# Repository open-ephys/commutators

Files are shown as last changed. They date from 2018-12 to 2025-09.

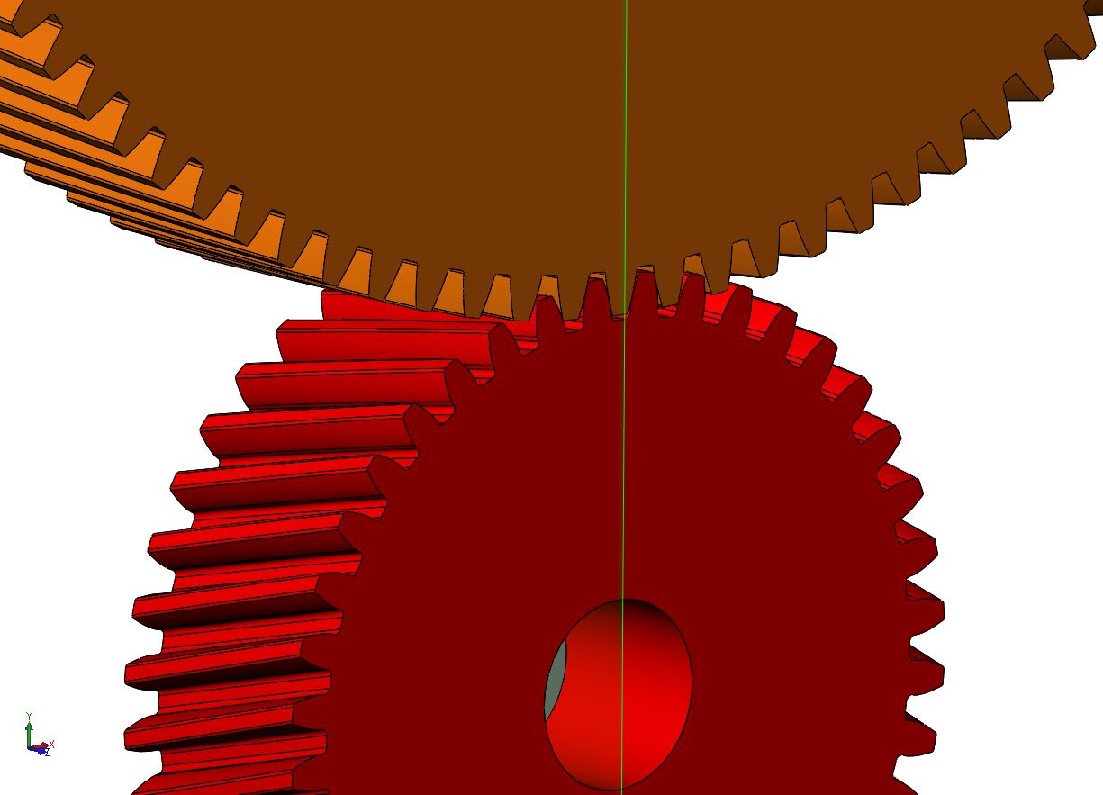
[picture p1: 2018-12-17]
mechanical/single_channel/gears/Robust Involute Helical Gear Generator.JPG

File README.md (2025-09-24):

> [!Important]  
> This repository has been split into dedicated repositories for each design:
>
>  - https://github.com/open-ephys/commutator-coax
>  - https://github.com/open-ephys/commutator-spi
>  - https://github.com/open-ephys/commutator-dual
>  - etc.
>
> Future commutator designs, issue tracking, etc. will take place in those repositories.
> This repository is deprecated.

# Torque-free commutators for orientation-aware headstages and miniscopes
The wide-spread availability of 6 degree of freedom pose tracking using
internal-measurement units (IMUs) allows continuous monitoring of an animal's
rotational state in an environment. This obviates the need for tether torque
measurements to drive an active commutator since the rotational state of the
animal is known in real-time, and the commutator can simply follow along. This
permits the use of extremely thin [coaxial
tethers](http://www.axon-cable.com/en/02_products/06_coaxial-cables/02/index.aspx)
that cannot function with a standard active commutator because they are too
flexible to translate rotational torque.

Zero-torque coaxial commutator.

This commutator functions with headstages and miniscopes that provide
provide appropriate rotational tracking information. Currently
supported devices are next-generation, serialized headstages and miniscopes
such as [ONIX headstages](https://open-ephys.github.io/onix-docs/index.html), 
and UCLA Miniscope 4.0, and Open Ephys 3D low-profile SPI headstages.
However, this device operations completely independently from the headstage
itself, so can be used with any device that provides accurate, drift-free
rotational state. It can even be used without an IMU, e.g. using video-based
rotation tracking since its remote control interface is agnostic to how
rotational measurements are taken.

## Features
- Variants for high bandwidth RF links up to 18 GHz and low-bandwidth SPI cables
- Optical table & 80/20 rail mountable
- Remote control using JSON-encoded commands
- Manual control using capacitive sense buttons
- Indication LED
    - Can be completely turned off
- Advanced stepper driver (TMC2130)
    - Voltage-controlled for silent operation
    - Precise motion using step interpolation (256 uSteps/step)
- USB powered and controlled
    - Internal super-capacitor circuitry prevents loading the USB bus during
      motion

## Usage

**Note**: A high-quality, within-spec micro USB cable must be used when connecting 
the commutator to the host computer.

### LED
The LED tells you about the commutator state:

1. Flashing red (*Charging*): commutator is charging internal super-capacitors.
   All controls and motor operation are locked. Wait until this process
   completes to use the device. It can take up to 30 seconds.
1. Solid red (*Disabled*): commutator is disabled. Motor is turned off and will not
   turn or respond to button presses or external commands.
1. Green (*Enabled*): commutator is enabled and permits both remote and manual
   (button) turn control. Buttons take precedence over remote commands.

### Buttons
The front panel has four buttons.

- __Enable/Disable__: toggle commutator enable/disable.
    - *Disabled* (LED is red): All motor output will halt instantly, and motor
      driver is powered down. Pressing directional buttons in the stopped state
      will not work. All target turns provided via remote calls will be
      cleared, such that re-enable the motor will not result in the commutator
      re-engaging an old target position. In this state, pressing 
      the Enable/Disable button, or sending the approriate remote
      command, will enable the device.
    - *Enabled* (LED  green): When in the *enabled* state, the LED will be
      green and the motor can be turned via button presses or RPCs . In this
      state, pressing the Stop/Go button, or sending the approriate remote
      command, will instantly disable the device.

- __Directional__ (2x): Manually control the motor rotation in the
  direction indicated on each button when the commutator is *Enabled*. These
  inputs take precedence over and override ongoing remote motor control.  When
  pressed, all target turns provided via remote control will be cleared, such
  that releasing them will not result in the commutator re-engaging an old
  target position. Remote commands sent when a button is being pressed are
  ignored.

- __LED__: pressing the LED will toggled on and off (e.g for cases where it presents an
  unwanted visual stimulus).

### Remote control interface
When manual buttons are not being pressed, the commutator accepts JSON-encoded
commands over its serial interface. Here are examples of all commands that can
be sent:
```
{enable : true}     // Enable commutator (default = false)
{led : false}       // Turn off RGB LED (default = true)
{speed : 250}       // Set turn speed to 250 RPM (default = 50 RPM, valid ∈ (0, 500] RPM)
{turn : 1.1}        // 1.1 turns CW
{turn : -1.1}       // 1.1 turns CCW

// Example multi-command. Any combo can be used.
// In this case:
// 1. Turn LED off
// 1. Set speed to 25 RPM
// 2. Excecute 1.1 turns CC
// Ordering of commands does not matter, it is determined by the firmware
{led: false, speed: 25, turn : -1.1}
```
The communator state can be read using the `{print:}` command  which will
return a JSON object containing version, state, and motor parameters.

### Saving settings
All control and speed parameters, whether changed via the remote or manual
interface, are saved in non-volatile memory each time they are changed. The
device will start in the same state it was last used.

## Firmware
The controller firmware is located [here](./firmware/commutator). It runs on a
[Teensy lc](https://www.pjrc.com/store/teensylc.html). To compile
this firmware and program the microcontroller, you need the following
dependencies:

- [Arduino IDE](https://www.arduino.cc/en/Main/Software)
- [Teensyduino add-on](https://www.pjrc.com/teensy/td_download.html)
- [AccelStepper](https://www.airspayce.com/mikem/arduino/AccelStepper/)
- [Arduino JSON](https://arduinojson.org/)

The firmware can be uploaded to the device using the [Arduino
IDE](https://www.arduino.cc/en/Main/Software). _Note that you will need to add
the [Teensyduino add-on](https://www.pjrc.com/teensy/teensyduino.html) to to
the Arduino IDE to program the Teensy_. When installing Teensyduino, you should
opt to install all of the bundled libraries as well. This takes care of
installing `AccelStepper` library rather than having to install it manually.
ArduinoJSON can be installed through the Arduino IDE's package manager.

## Construction

### Bill of Materials
The BOM is located [here](https://docs.google.com/spreadsheets/d/1M2R0Q2-OuRHzctt05BxtA3hxNcCHtRZHORzCKElmG1Q/edit#gid=1283420334).

### Mechanical
The mechanical component of the commutator are as follows:

1. RF Rotary Joint
1. 2x reduction gears (3D-printed)
1. NEMA-11 Stepper Motor
1. Housing (3D-printed)
1. Some fasteners

Mechanical designs are located [here](./mechanical/). STL files for 3D printing
are located in the `stl` subdirectory. Links to purchase each of these
components, including 3D-printed parts, can be found on the BOM.

### Electronics
The board used to control the commutator consists of the following elements:

1. [Teensy LC](https://www.pjrc.com/store/teensylc.html) for receiving
   commands and controlling all circuit elements.
1. [TMC2130 stepper driver](https://www.analog.com/media/en/technical-documentation/data-sheets/TMC2130_datasheet_rev1.15.pdf) for driving the
   motor.
1. Super-capacitor charge system and step-up regulator for providing
   high-current capacity drive to the motor driver directly from USB.
1. RGB indicator LED.
1. Capacitive touch sensors on the back side of the PCB that serve as buttons
   for manual commutator control

Board designs and manufacturing files are located [here](./pcb/). 

## Hardware License
This license pertains to documents in the `control-board`, `mechanical`, and
`resources` subdirectory.

This work is licensed to Jonathan P. Newman and Jakob Voigts under CC BY-NC-SA
4.0. To view a copy of this license, visit
https://creativecommons.org/licenses/by-nc-sa/4.0

The creation of commercial products using the hardware documentation in this
repository is not permitted without an explicit, supplementary agreement
between the Licensor and the Licensee. Please get in touch if you are
interested in commercially distributing this tool.

## Software/Firmware License
This license pertains to documents in the source code in the `firmware`
subdirectory.

Copyright Jonathan P. Newman

Permission is hereby granted, free of charge, to any person obtaining a copy of
this software and associated documentation files (the "Software"), to deal in
the Software without restriction, including without limitation the rights to
use, copy, modify, merge, publish, distribute, sublicense, and/or sell copies
of the Software, and to permit persons to whom the Software is furnished to do
so, subject to the following conditions:

The above copyright notice and this permission notice shall be included in all
copies or substantial portions of the Software.

THE SOFTWARE IS PROVIDED "AS IS", WITHOUT WARRANTY OF ANY KIND, EXPRESS OR
IMPLIED, INCLUDING BUT NOT LIMITED TO THE WARRANTIES OF MERCHANTABILITY,
FITNESS FOR A PARTICULAR PURPOSE AND NONINFRINGEMENT. IN NO EVENT SHALL THE
AUTHORS OR COPYRIGHT HOLDERS BE LIABLE FOR ANY CLAIM, DAMAGES OR OTHER
LIABILITY, WHETHER IN AN ACTION OF CONTRACT, TORT OR OTHERWISE, ARISING FROM,
OUT OF OR IN CONNECTION WITH THE SOFTWARE OR THE USE OR OTHER DEALINGS IN THE
SOFTWARE.

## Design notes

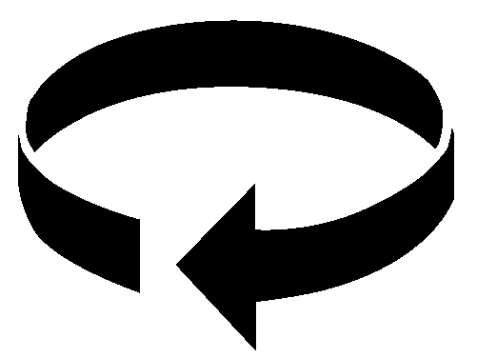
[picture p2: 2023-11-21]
pcb/images/turn-cw.png

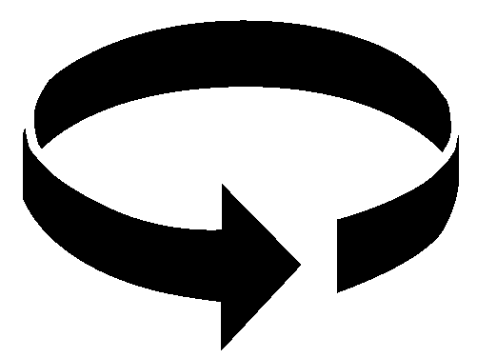
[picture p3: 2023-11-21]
pcb/images/turn-ccw.png

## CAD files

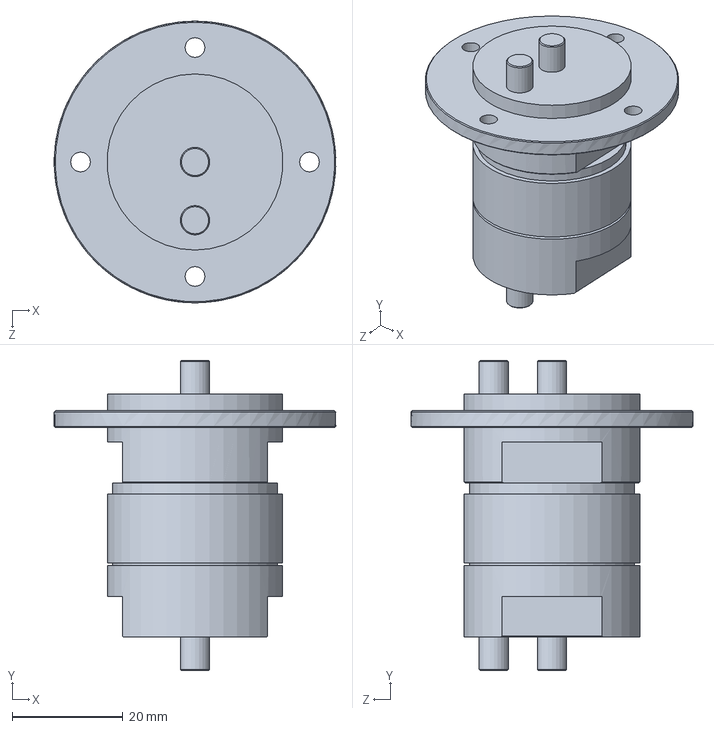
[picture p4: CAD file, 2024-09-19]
mechanical/dual_channel/BN_153127C0001_rotary_joint.SLDPRT
50.8 x 55.9 x 50.8 mm

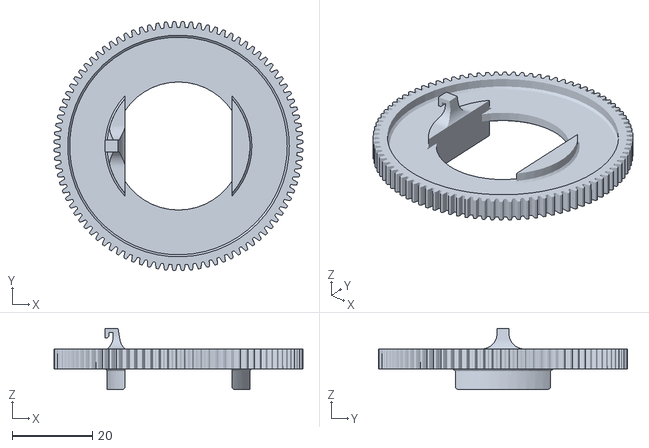
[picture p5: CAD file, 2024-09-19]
mechanical/dual_channel/STL/gear_b_dual_channel.STL
62.0 x 62.0 x 15.3

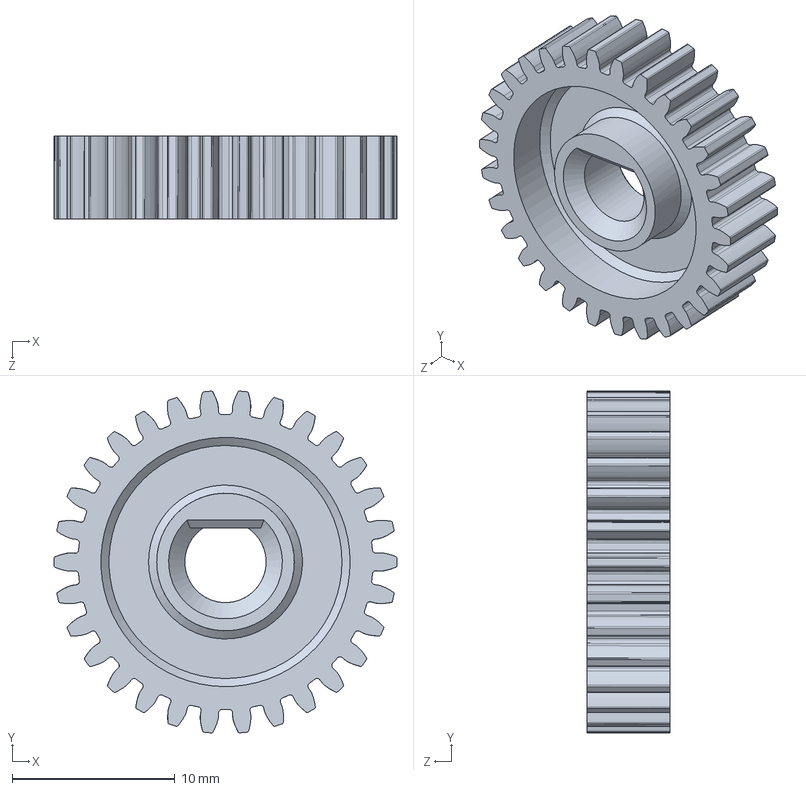
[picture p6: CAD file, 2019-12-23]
mechanical/single_channel/gears/gear_a.SLDPRT
21.1 x 21.0 x 5.08 mm

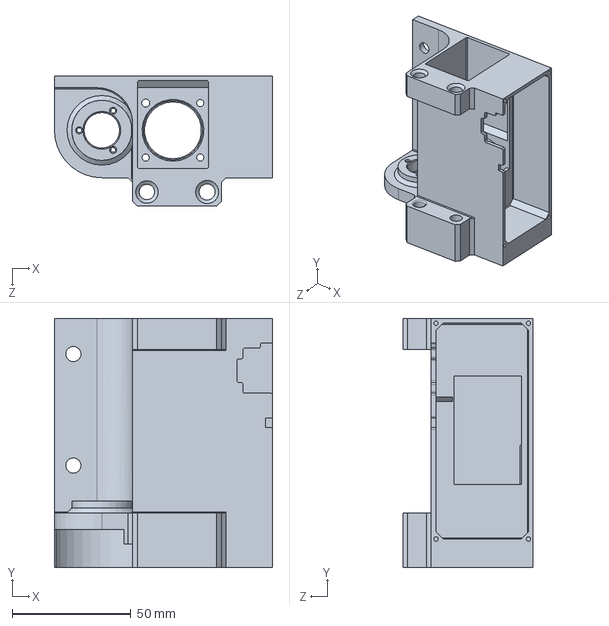
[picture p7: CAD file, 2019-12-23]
mechanical/single_channel/rf_commutator_housing.SLDPRT
92.0 x 105.0 x 55.0 mm

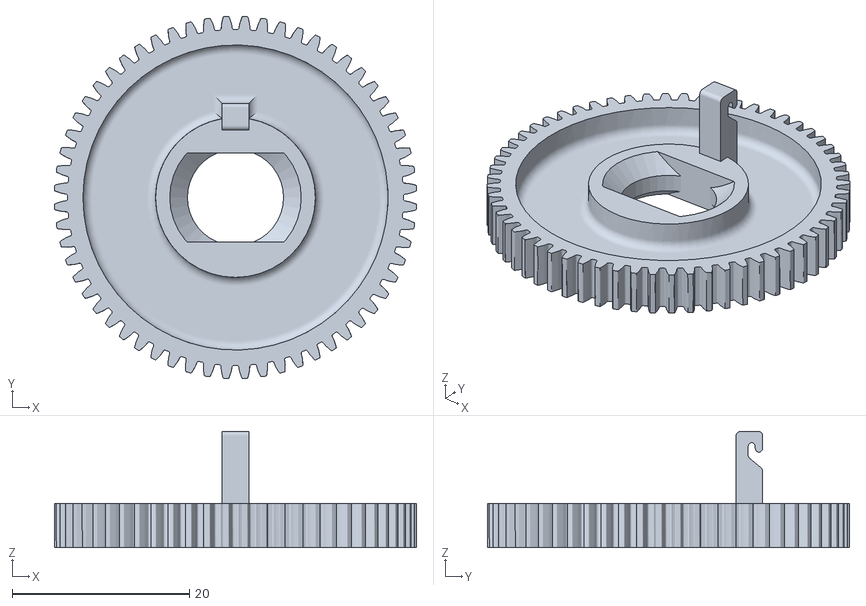
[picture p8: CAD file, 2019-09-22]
mechanical/single_channel/stl/gear_b.STL
40.9 x 40.9 x 13.1

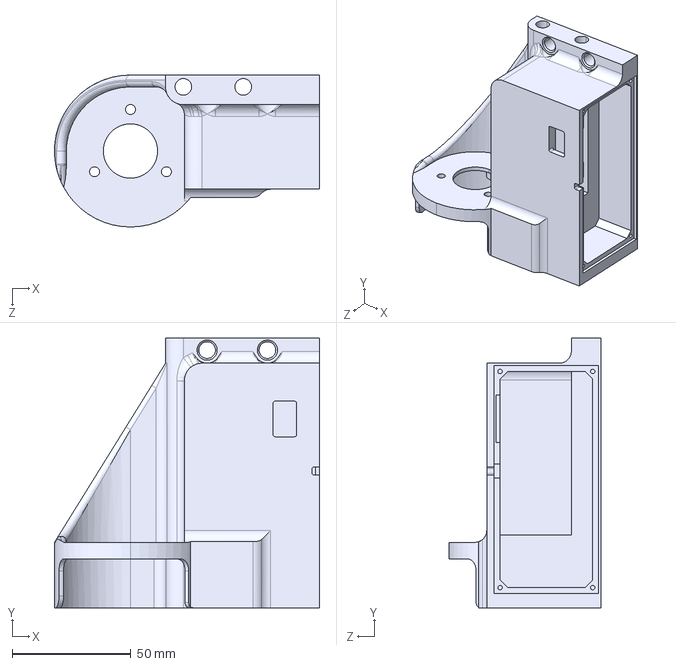
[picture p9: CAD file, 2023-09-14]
mechanical/spi/production/SPI Commutator Enclosure Motor Enclosed.STEP
111.6 x 113.5 x 64.0 mm

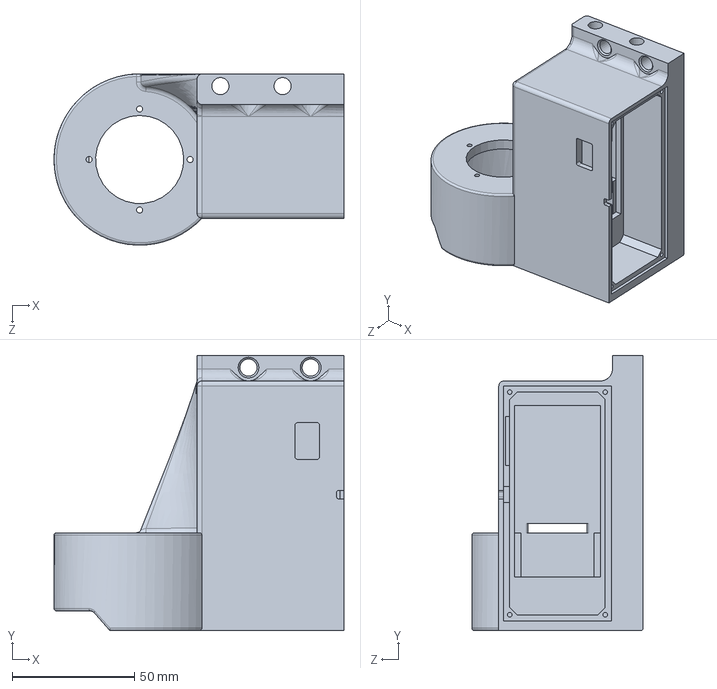
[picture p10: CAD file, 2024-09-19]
mechanical/dual_channel/dual_channel_commutator_housing.SLDPRT
118.5 x 112.5 x 70.0 mm

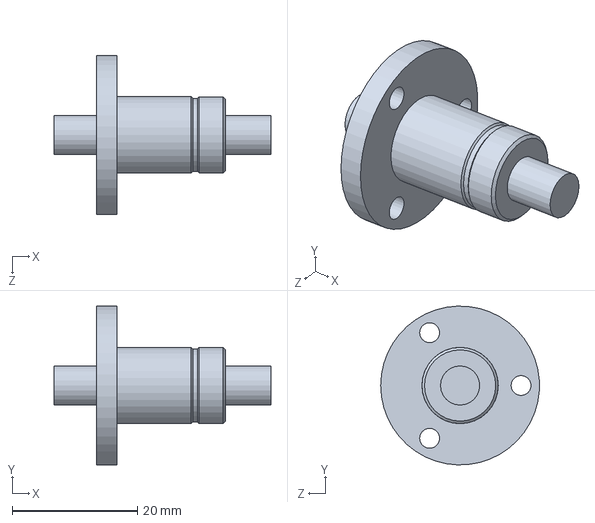
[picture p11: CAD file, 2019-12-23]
mechanical/single_channel/Fairview_FMRJ1002_rf_rotary_jpint_female_to_female_flanged.SLDPRT
34.7 x 25.4 x 25.4 mm

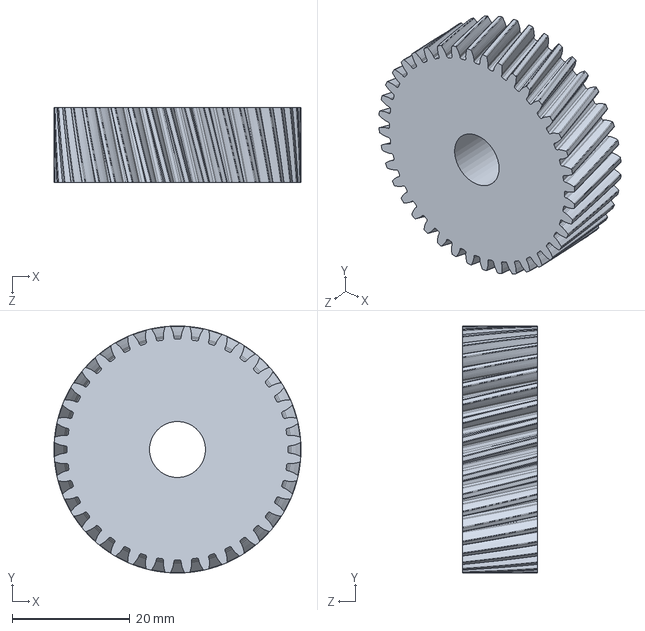
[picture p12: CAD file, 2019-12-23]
mechanical/single_channel/gears/Robust Involute Helical Gear Generator - CCW.SLDPRT
42.0 x 42.0 x 12.7 mm

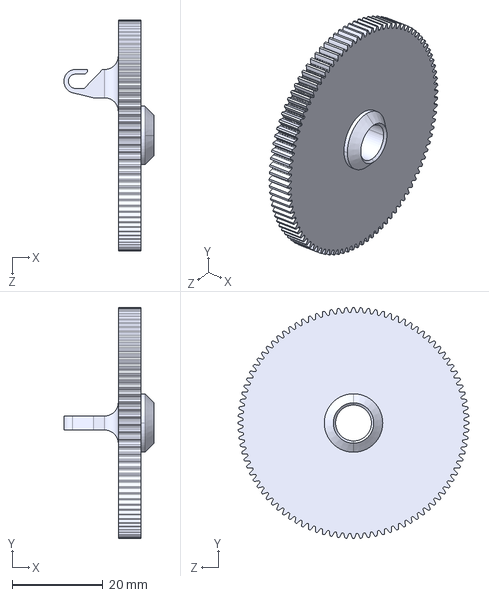
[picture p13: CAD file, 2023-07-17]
mechanical/spi/production/SI_sdpsi_s12a05m096n0310 cut.STEP
19.9 x 51.0 x 51.0 mm

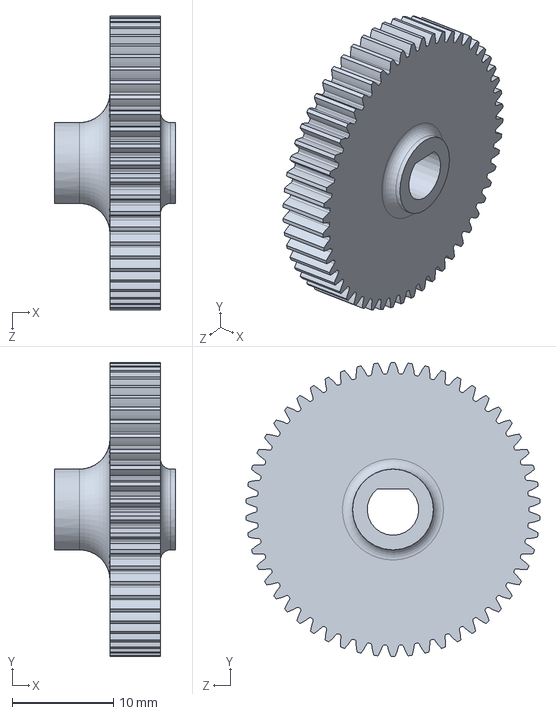
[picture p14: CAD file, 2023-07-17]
mechanical/spi/source/SI_sdpsi_s12a05m054n0310 cut.SLDPRT
12.0 x 29.1 x 29.1 mm

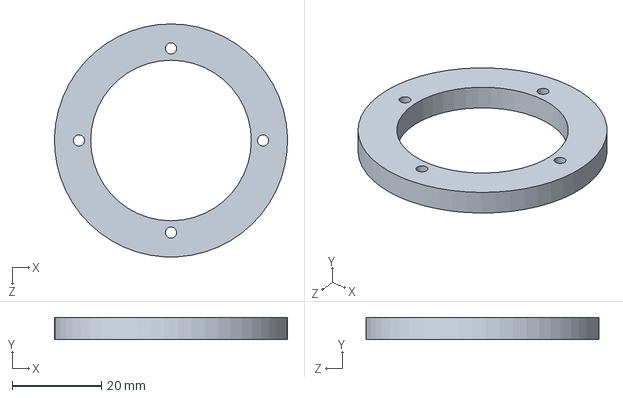
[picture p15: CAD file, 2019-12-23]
mechanical/dual_channel/dual_channel_commuttaor_housing.SLDPRT
52.2 x 5.00 x 52.3 mm

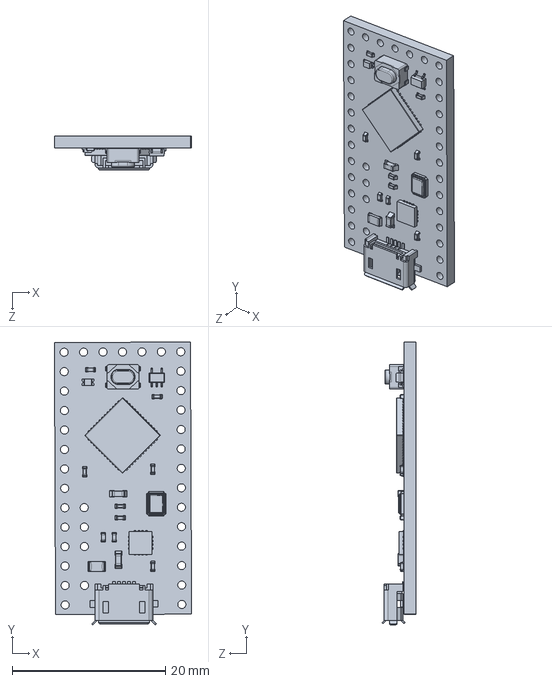
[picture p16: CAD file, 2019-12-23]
mechanical/single_channel/Teensy_lc.SLDPRT
17.9 x 37.0 x 4.49 mm

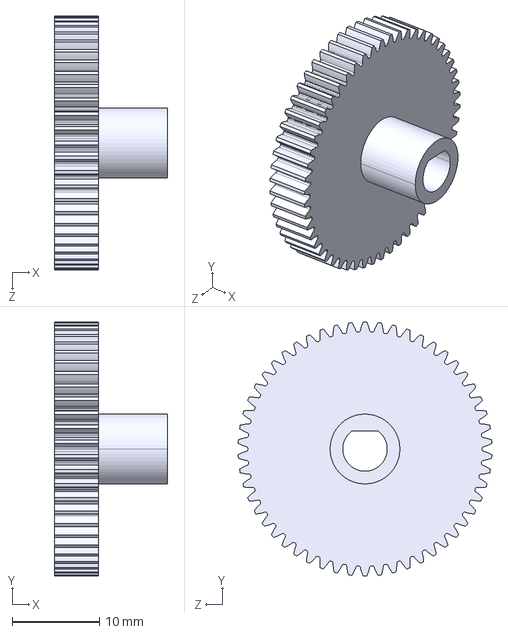
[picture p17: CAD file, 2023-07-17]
mechanical/spi/production/SI_sdpsi_s12a05m054n0310 cut.STEP
13.0 x 29.1 x 29.1 mm

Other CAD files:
mechanical/spi/source/SPI Commutator Enclosure Motor Enclosed.SLDPRT
mechanical/single_channel/stl/gear_a.STL
mechanical/single_channel/gears/gear_b.STL
mechanical/spi/source/SI_sdpsi_s12a05m096n0310 cut.STEP
mechanical/dual_channel/STL/dual_channel_commutator_housing.STL
mechanical/single_channel/6627T370_POSITION-CONTROL DC MOTOR.SLDPRT
mechanical/single_channel/CUI_PJ-102A.SLDPRT
mechanical/single_channel/CUI_PJ-102A.STEP
mechanical/single_channel/DRV 8825 With Headers Assem.SLDPRT
mechanical/single_channel/DRV 8825 With Headers Assem.STEP
mechanical/single_channel/Fairview_FMRJ1001_rf_rotary_jpint_female_to_female.SLDPRT
mechanical/single_channel/Teensy_lc.stp
mechanical/single_channel/pulley_large.SLDPRT
mechanical/single_channel/pulley_small.SLDPRT
mechanical/single_channel/spinner_BN-835047C0010_rf_rotary_joint.SLDPRT
mechanical/single_channel/stl/rf_commutator_housing.STL
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

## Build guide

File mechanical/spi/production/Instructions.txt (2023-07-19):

Printing Methods:
Gears - SLA
Enclosure - SLS

The gears are glued to the Orbex and motor shafts

Set gear ratio (16.0/9.0) using the GEAR_RATIO macro found on line 22 of https://github.com/open-ephys/onix-commutator/blob/master/firmware/commutator/commutator.ino (this is valid since commit f684f83; this could change if commutator firmware is updated)

All 11 holes need to be tapped. I'm not sure how OEPS does it for the Coax Commutator, but I assume whatever tool you use for that can be used for tapping the holes on the coax commutator
@Jon Newman I don't think I missed anything, but if you have anything add ^ feel free

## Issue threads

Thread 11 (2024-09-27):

### ISSUE TITLE
Teensy 3.2 and LC EOL 

### ISSUE THREAD

**Issue by jonnew** [open-ephys/commutators#11]
Both the Teensy LC and 3.2 are end of lifed. We will need to migrate to a different microcontroller option. Most MCUs don't come with integrated capacitive touch sensing. Additionally it has proven to be quite a difficult thing to get working reliably. However, it reducing design complexity and is appropriate for environments with animals. An option would be switching to some relatively generic MCU, e.g. RP2040 and adding an external cap sensor that hopefully takes care of the calibration issues for us. @aacuevas suggests the following: 

- https://ww1.microchip.com/downloads/aemDocuments/documents/OTH/ProductDocuments/DataSheets/00001571B.pdf

Microchip seems to have a family of those, which is a good thing for future-proofing. And it's a bit under a dollar and a half. In any case, it will need to be tested.

**Comment by jonnew** [comment]
Some measurements of GND referenced capacitance at on the V1.1 PCB

|   | 1 kHz   |
|---|---|
| LED Button  | 14 pF   | 
| Left Turn  |  51 pF | 
| Right Turn | 45 pF  | 
| Enable/Disable   | 42 pF  | 

This is right at the limit for the chip suggested above:

![image](https://github.com/user-attachments/assets/a6db75b4-fe4f-400c-8482-b05cc65772db)

Might be work decreasing this bit (e.g. by mesh filling the copy islands of the big buttons with ~50 fill density)

**Comment by cjsha** [comment]
Thanks for taking those measurements, I'll try the 50% mesh fill. That's also suggested by:
[Capacitive-Touch-Sensor-Design-Guide-DS00002934-B.pdf](https://github.com/user-attachments/files/17078185/Capacitive-Touch-Sensor-Design-Guide-DS00002934-B.pdf)
![Screenshot_20240920-123908](https://github.com/user-attachments/assets/18e2195d-66f2-4194-952a-0a322f52d42f)

**Comment by jonnew** [comment]
Nice, that guide is cool.

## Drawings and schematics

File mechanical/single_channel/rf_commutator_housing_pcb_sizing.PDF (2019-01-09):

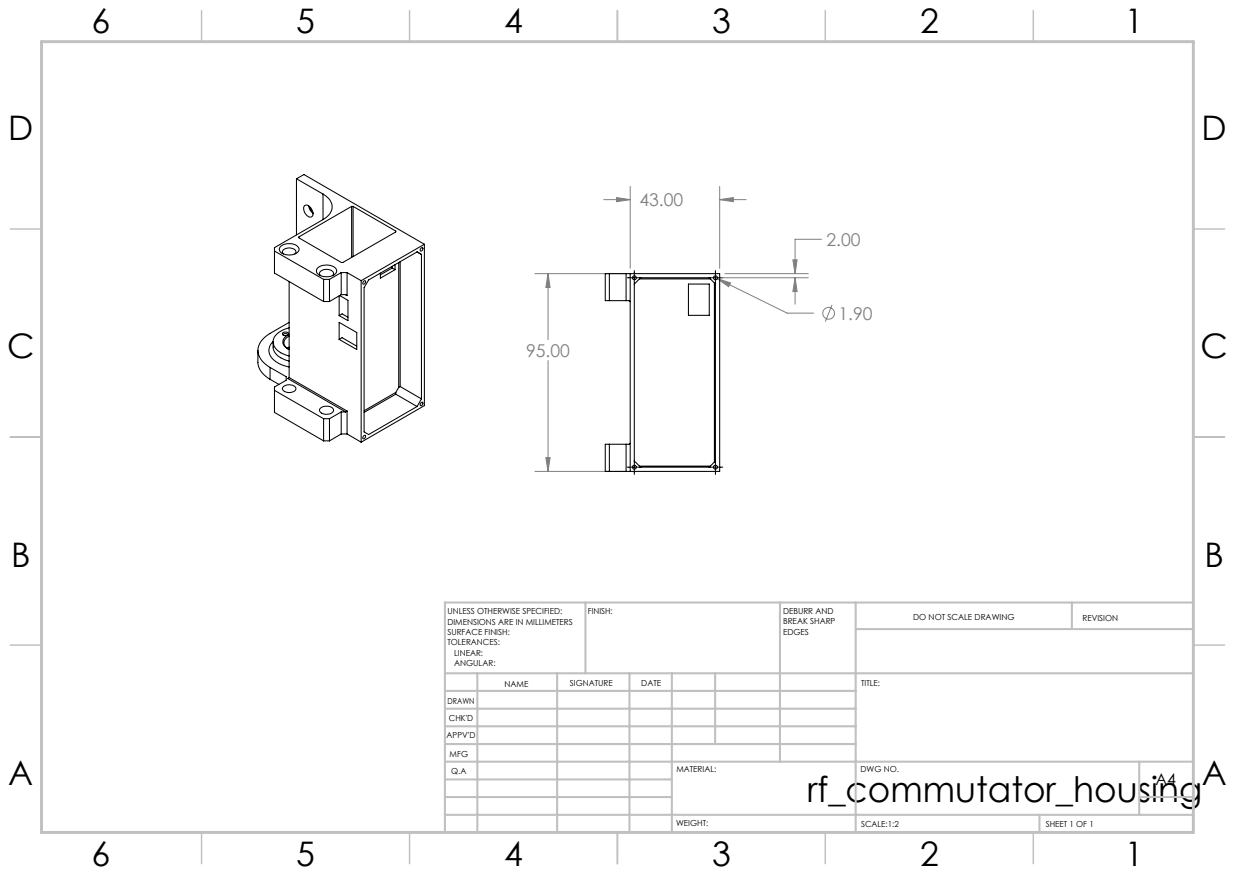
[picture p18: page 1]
FINISH:; DEBURR AND; BREAK SHARP; DO NOT SCALE DRAWING; REVISION; SCALE:1:2; SHEET 1 OF 1

UNLESS OTHERWISE SPECIFIED:
DIMENSIONS ARE IN MILLIMETERS
SURFACE FINISH:
TOLERANCES:
LINEAR:
ANGULAR:

NAME | SIGNATURE | DATE | | | | TITLE:

DRAWN
CHK'D
APPV'D
MFG
Q.A | | | | MATERIAL: | DWG NO. | A4

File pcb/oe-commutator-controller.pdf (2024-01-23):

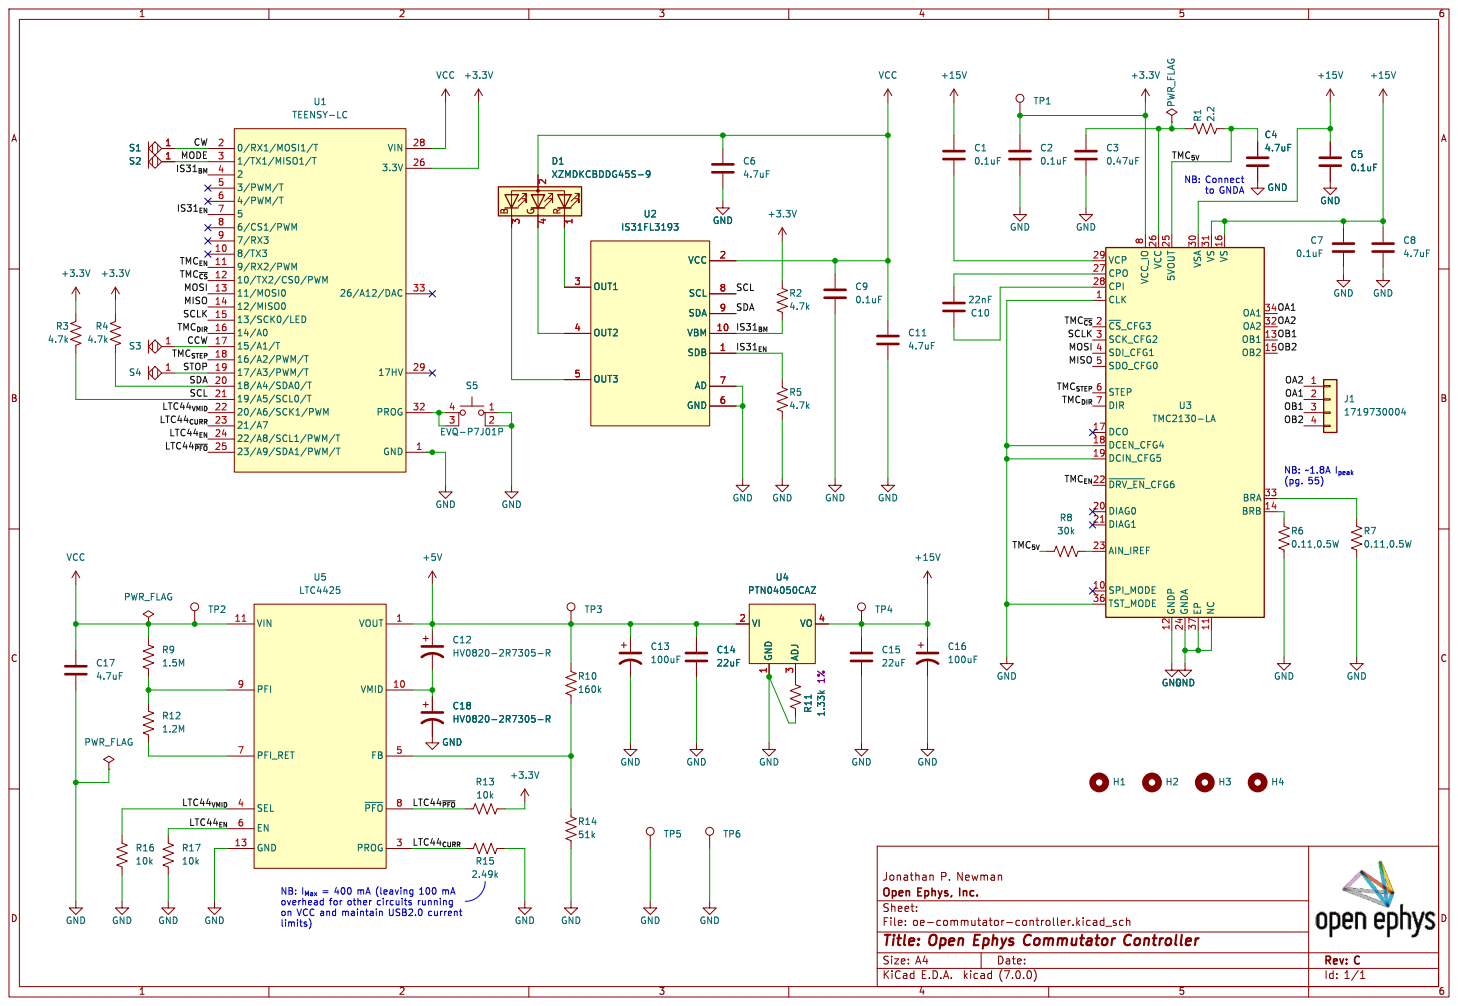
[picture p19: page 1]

(pg. 55) NB: I_{Max} = 400 mA (leaving 100 mA

overhead for other circuits running
on VCC and maintain USB2.0 current
limits)

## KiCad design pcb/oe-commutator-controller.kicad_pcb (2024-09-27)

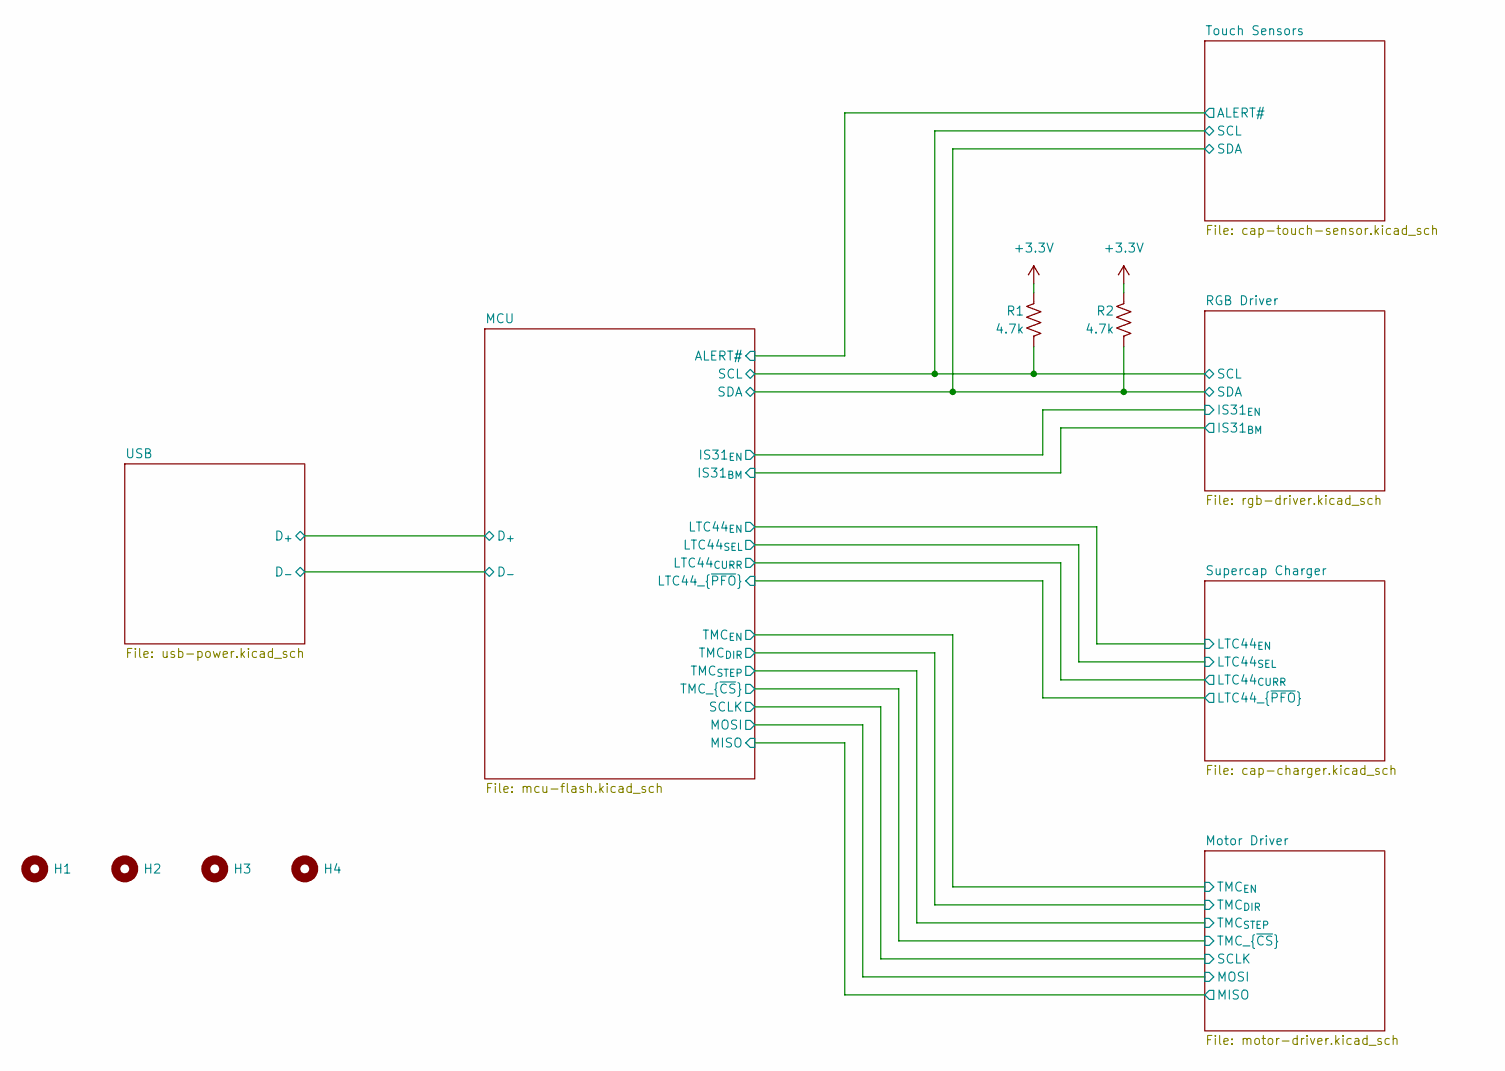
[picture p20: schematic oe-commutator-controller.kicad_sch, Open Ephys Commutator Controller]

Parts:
H1, H2, H3, H4: MountingHole_2.7mm_M2.5_ISO7380
R1, R2: 4.7k; R_0603_1608Metric

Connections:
+3.3V: R1.1, R2.1; also elsewhere on the board
/MCU/SCL: R1.2; also elsewhere on the board
/MCU/SDA: R2.2; also elsewhere on the board

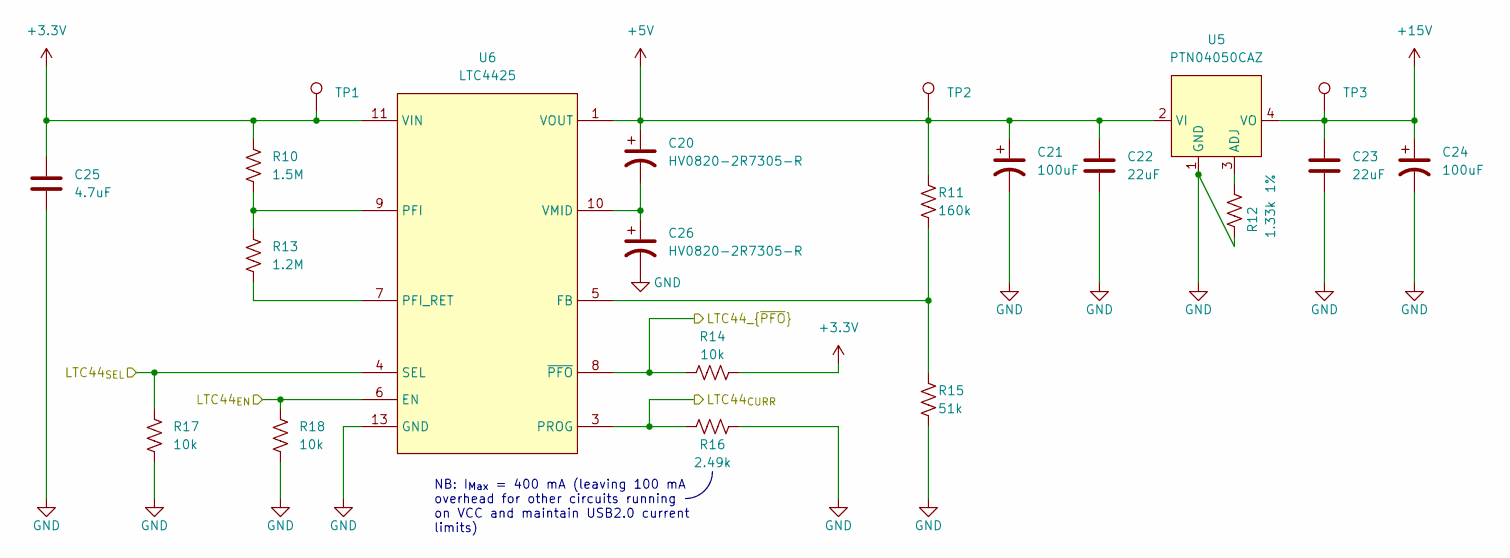
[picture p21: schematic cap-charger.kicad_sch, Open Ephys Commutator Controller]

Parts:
C20, C26: HV0820-2R7305-R; C_1210_3225Metric
C21, C24: 100uF; C_Elec_8x10.2
C22, C23: 22uF; C_1206_3216Metric
C25: 4.7uF; C_0805_2012Metric
R10: 1.5M; R_0603_1608Metric
R11: 160k; R_0603_1608Metric; Tolerance 1%
R12: 1.33k; R_0603_1608Metric; Tolerance 1%
R13: 1.2M; R_0603_1608Metric
R14, R17, R18: 10k; R_0603_1608Metric
R15: 51k; R_0603_1608Metric; Tolerance 1%
R16: 2.49k; R_0603_1608Metric
TP1, TP2, TP3: TestPoint_Pad_D2.0mm
U5: PTN04050CAZ; TI_R-PDSS_B4_SMD
U6: LTC4425; MSOP-12-1EP_3x4mm_P0.65mm_EP1.65x2.85mm

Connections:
+3.3V: C25.1, R10.1, R14.2, TP1.1, U6.11 (VIN), U6.12 (VIN); also elsewhere on the board
+5V: C20.1, C21.1, C22.1, R11.1, TP2.1, U5.2 (VI), U6.1 (VOUT), U6.2 (VOUT)
+15V: C23.1, C24.1, TP3.1, U5.4 (VO); also elsewhere on the board
/MCU/LTC44_{CURR}: R16.2, U6.3 (PROG); also elsewhere on the board
/MCU/LTC44_{EN}: R18.1, U6.6 (EN); also elsewhere on the board
/MCU/LTC44_{SEL}: R17.1, U6.4 (SEL); also elsewhere on the board
/MCU/LTC44_{~PFO}: R14.1, U6.8 (~PFO); also elsewhere on the board
GND: C21.2, C22.2, C23.2, C24.2, C25.2, C26.2, R12.2, R15.2, R16.1, R17.2, R18.2, U5.1 (GND), U6.13 (GND); also elsewhere on the board
unnamed: R12.1, U5.3 (ADJ)
unnamed: R11.2, R15.1, U6.5 (FB)
unnamed: R10.2, R13.1, U6.9 (PFI)
unnamed: R13.2, U6.7 (PFI_RET)
unnamed: C20.2, C26.1, U6.10 (VMID)

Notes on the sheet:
NB: I_{Max} = 400 mA (leaving 100 mA overhead for other circuits running on VCC and maintain USB2.0 current limits)

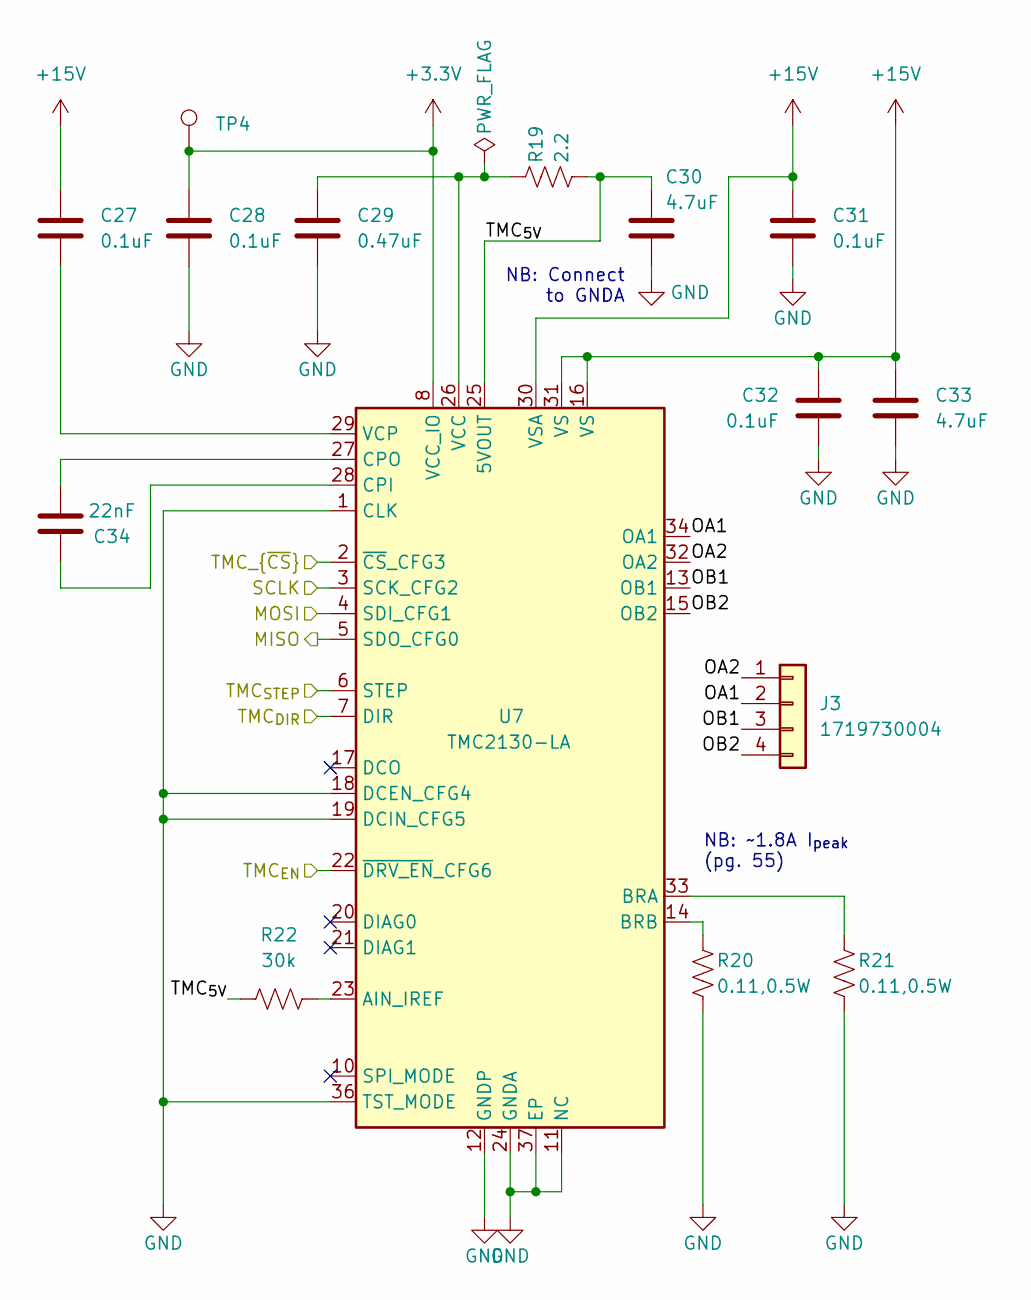
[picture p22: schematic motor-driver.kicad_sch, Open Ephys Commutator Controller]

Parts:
C27, C28, C31, C32: 0.1uF; C_0603_1608Metric; Voltage 50V
C29: 0.47uF; C_0805_2012Metric; Voltage 50V
C30, C33: 4.7uF; C_0805_2012Metric; Voltage 50V
C34: 22nF; C_0603_1608Metric; Voltage 50V
J3: 1719730004; MOLEX_1719730004_1x04_P2.54mm_Vert_Lock
R19: 2.2; R_0603_1608Metric
R20, R21: 0.11,0.5W; R_1206_3216Metric
R22: 30k; R_0603_1608Metric
TP4: TestPoint_Pad_D2.0mm
U7: TMC2130-LA; QFN-36-1EP_5x6mm_P0.5mm_EP3.6x4.1mm

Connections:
+3.3V: C28.1, TP4.1, U7.8 (VCC_IO); also elsewhere on the board
+15V: C27.2, C31.2, C32.2, C33.2, U7.16 (VS), U7.30 (VSA), U7.31 (VS); also elsewhere on the board
/MCU/MISO: U7.5 (SDO_CFG0); also elsewhere on the board
/MCU/MOSI: U7.4 (SDI_CFG1); also elsewhere on the board
/MCU/SCLK: U7.3 (SCK_CFG2); also elsewhere on the board
/MCU/TMC_{DIR}: U7.7 (DIR); also elsewhere on the board
/MCU/TMC_{EN}: U7.22 (~DRV_EN_CFG6); also elsewhere on the board
/MCU/TMC_{STEP}: U7.6 (STEP); also elsewhere on the board
/MCU/TMC_{~CS}: U7.2 (~CS_CFG3); also elsewhere on the board
/Motor Driver/OA1: J3.2, U7.34 (OA1)
/Motor Driver/OA2: J3.1, U7.32 (OA2)
/Motor Driver/OB1: J3.3, U7.13 (OB1)
/Motor Driver/OB2: J3.4, U7.15 (OB2)
/Motor Driver/TMC_{5V}: C30.2, R19.2, R22.1, U7.25 (5VOUT)
GND: C28.2, C29.2, C30.1, C31.1, C32.1, C33.1, R20.2, R21.2, U7.1 (CLK), U7.11 (NC), U7.12 (GNDP), U7.18 (DCEN_CFG4), U7.19 (DCIN_CFG5), U7.24 (GNDA), U7.35 (GNDP), U7.36 (TST_MODE), U7.37 (EP); also elsewhere on the board
unnamed: R22.2, U7.23 (AIN_IREF)
unnamed: R21.1, U7.33 (BRA)
unnamed: R20.1, U7.14 (BRB)
unnamed: C34.2, U7.28 (CPI)
unnamed: C34.1, U7.27 (CPO)
unnamed: C29.1, R19.1, U7.26 (VCC)
unnamed: C27.1, U7.29 (VCP)

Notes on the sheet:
NB: ~1.8A I_{peak} (pg. 55)
NB: Connect to GNDA

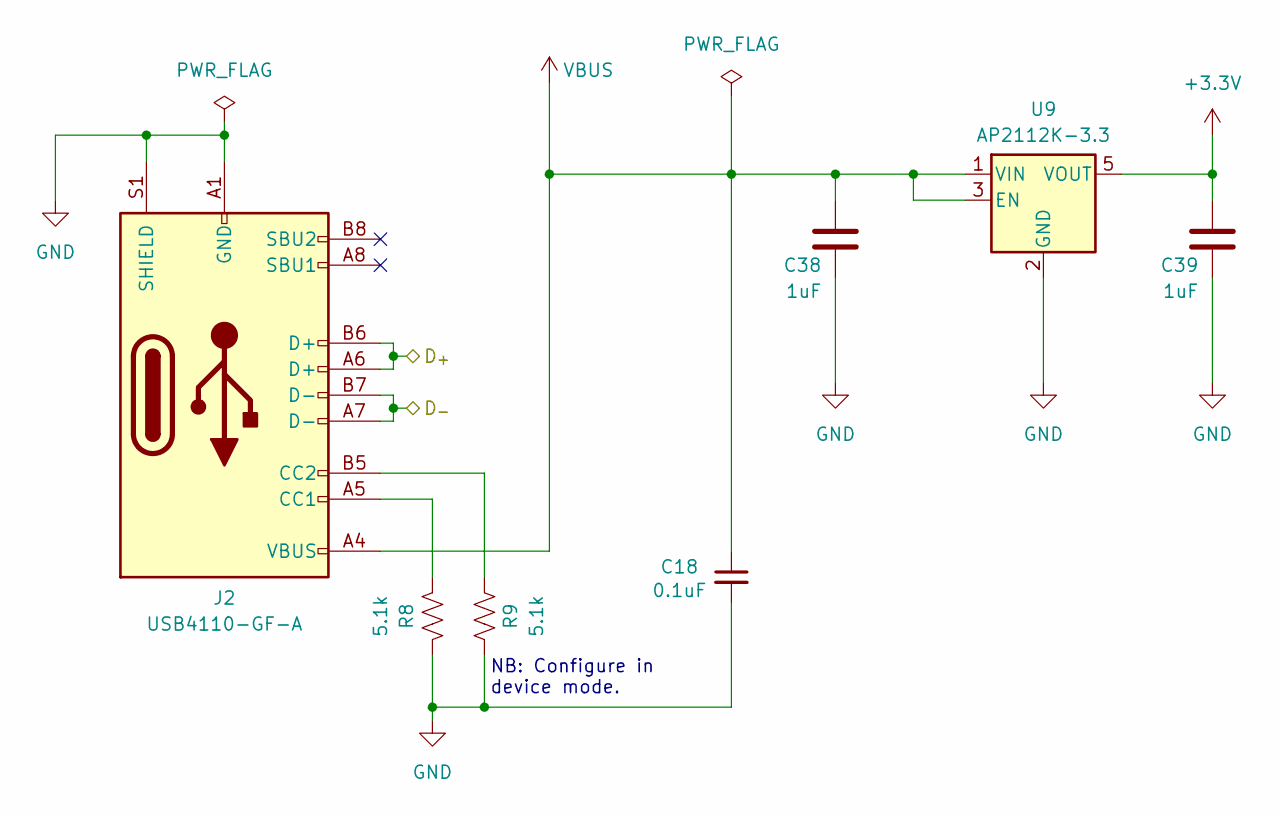
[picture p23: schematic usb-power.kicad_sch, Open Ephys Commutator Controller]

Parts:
C18: 0.1uF; C_0603_1608Metric
C38, C39: 1uF; C_0603_1608Metric
J2: USB4110-GF-A; USB_C_Receptacle_GCT_USB4110
R8, R9: 5.1k; R_0402_1005Metric
U9: AP2112K-3.3; SOT-23-5

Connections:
+3.3V: C39.1, U9.5 (VOUT); also elsewhere on the board
/MCU/D_{+}: J2.A6 (D+), J2.B6 (D+); also elsewhere on the board
/MCU/D_{-}: J2.A7 (D-), J2.B7 (D-); also elsewhere on the board
GND: C18.2, C38.2, C39.2, J2.A1 (GND), J2.A12 (GND), J2.B1 (GND), J2.B12 (GND), J2.S1 (SHIELD), R8.1, R9.1, U9.2 (GND); also elsewhere on the board
unnamed: J2.A5 (CC1), R8.2
unnamed: J2.B5 (CC2), R9.2
VBUS: C18.1, C38.1, J2.A4 (VBUS), J2.A9 (VBUS), J2.B4 (VBUS), J2.B9 (VBUS), U9.1 (VIN), U9.3 (EN)

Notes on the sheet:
NB: Configure in device mode.

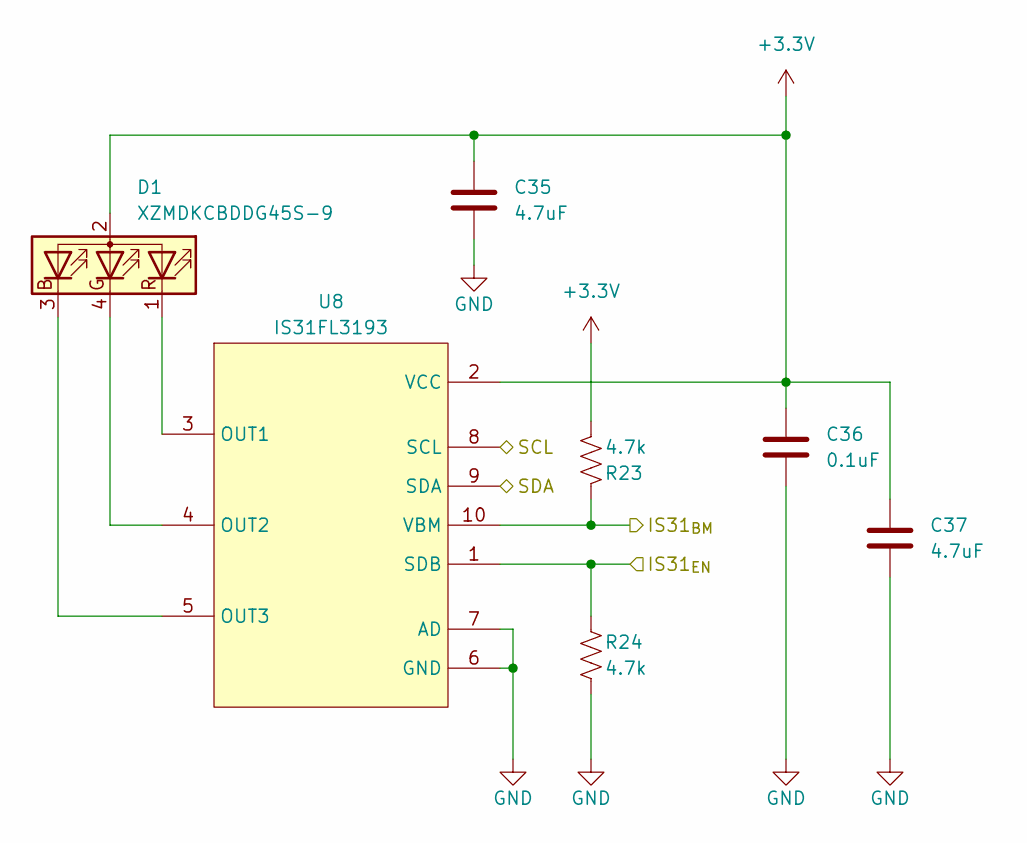
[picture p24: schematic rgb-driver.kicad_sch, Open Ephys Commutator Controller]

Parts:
C35, C37: 4.7uF; C_0805_2012Metric
C36: 0.1uF; C_0603_1608Metric; Voltage 50V
D1: XZMDKCBDDG45S-9; SUNLED_PLCC4-INV_3.2x2.8x1.9mm
R23, R24: 4.7k; R_0603_1608Metric
U8: IS31FL3193; DFN-10-1EP_3x3mm_P0.5mm_EP1.65x2.38mm

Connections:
+3.3V: C35.1, C36.1, C37.1, D1.2 (A), R23.2, U8.2 (VCC); also elsewhere on the board
/MCU/IS31_{BM}: R23.1, U8.10 (VBM); also elsewhere on the board
/MCU/IS31_{EN}: R24.1, U8.1 (SDB); also elsewhere on the board
/MCU/SCL: U8.8 (SCL); also elsewhere on the board
/MCU/SDA: U8.9 (SDA); also elsewhere on the board
GND: C35.2, C36.2, C37.2, R24.2, U8.6 (GND), U8.7 (AD), U8.11 (GND); also elsewhere on the board
unnamed: D1.3 (BK), U8.5 (OUT3)
unnamed: D1.4 (GK), U8.4 (OUT2)
unnamed: D1.1 (RK), U8.3 (OUT1)

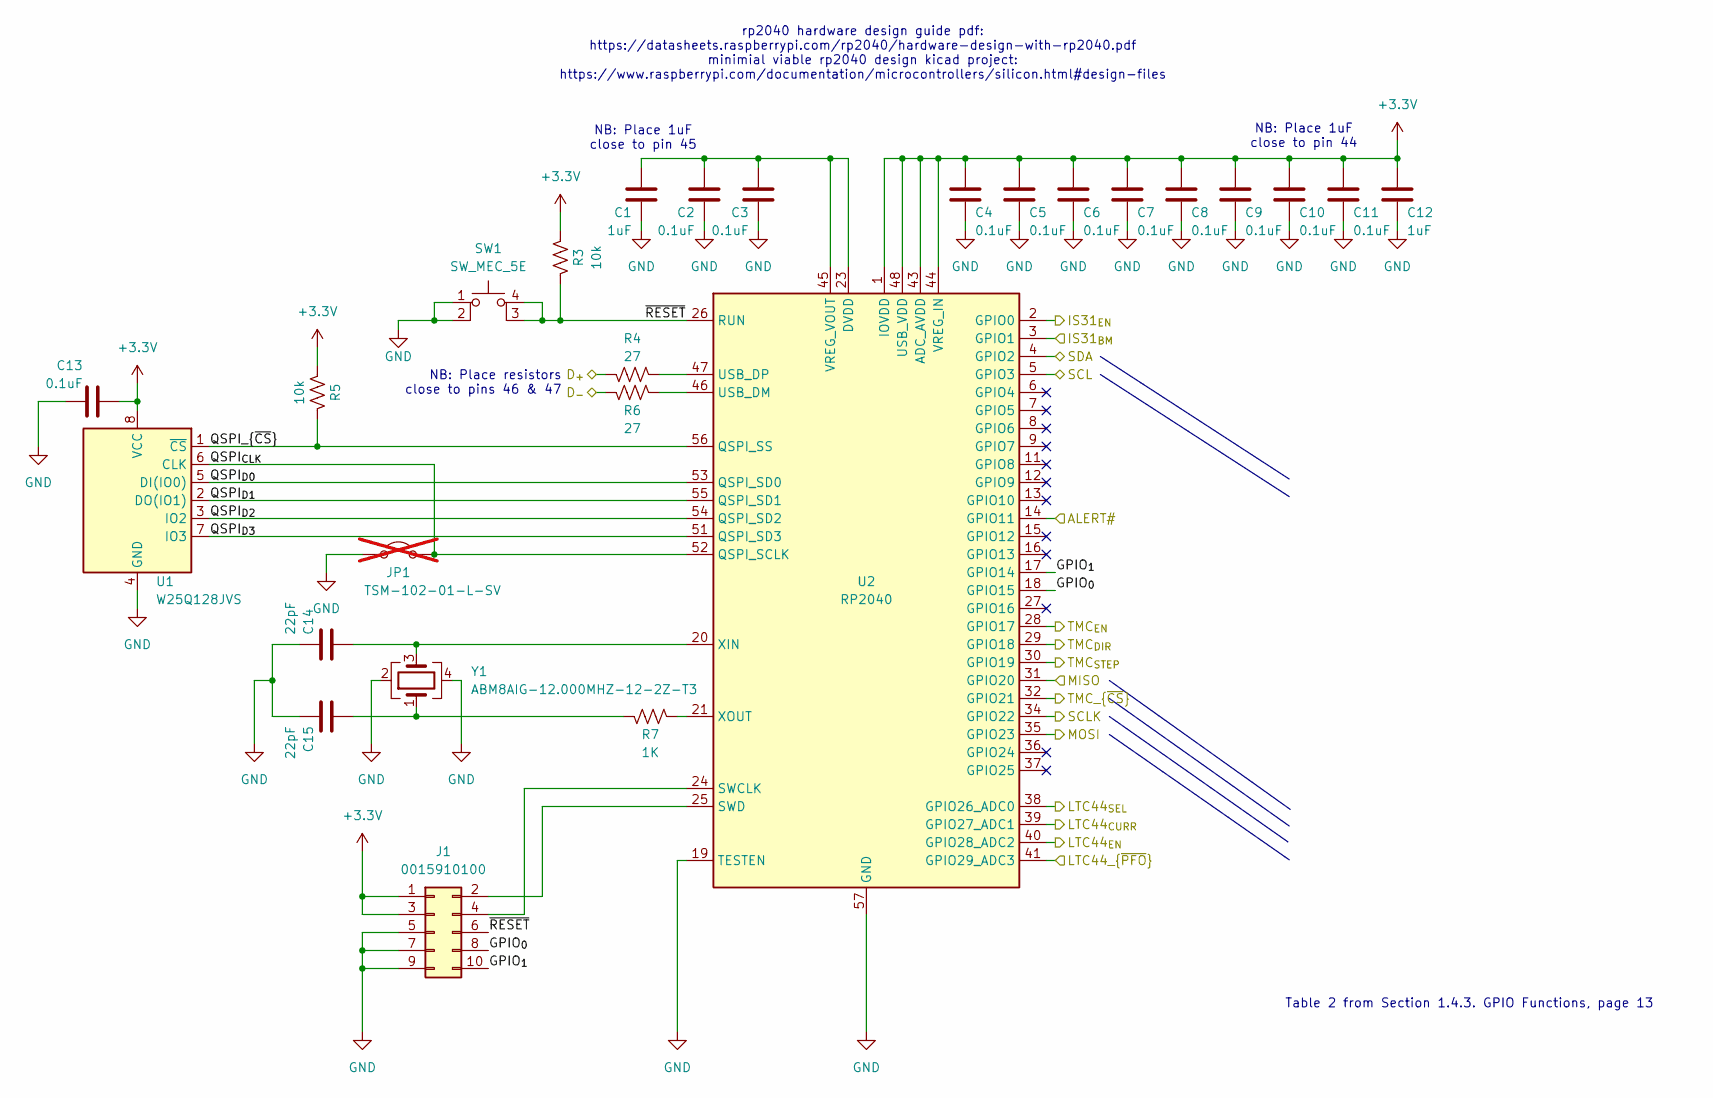
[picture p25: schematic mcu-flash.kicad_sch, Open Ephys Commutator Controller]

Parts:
C1, C12: 1uF; C_0603_1608Metric
C2, C3, C4, C5, C6, C7, C8, C9, C10, C11, C13: 0.1uF; C_0402_1005Metric
C14, C15: 22pF; C_0402_1005Metric
J1: 0015910100; PinHeader_2x05_P2.54mm_Vertical_SMD
JP1: TSM-102-01-L-SV; PinHeader_1x02_P2.54mm_Vertical_SMD_Pin1Left; not fitted
R3, R5: 10k; R_0402_1005Metric
R4, R6: 27; R_0402_1005Metric
R7: 1K; R_0402_1005Metric
SW1: SW_MEC_5E; PANASONIC_EVQP7-JA-01P
U1: W25Q128JVS; SOIC-8_5.23x5.23mm_P1.27mm
U2: RP2040; QFN-56-1EP_7x7mm_P0.4mm_EP3.2x3.2mm
Y1: ABM8AIG-12.000MHZ-12-2Z-T3; Crystal_SMD_Abracon_ABM8AIG-4Pin_3.2x2.5mm

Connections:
+3.3V: C4.1, C5.1, C6.1, C7.1, C8.1, C9.1, C10.1, C11.1, C12.1, C13.1, J1.1, J1.3, R3.1, R5.1, U1.8 (VCC), U2.1 (IOVDD), U2.10 (IOVDD), U2.22 (IOVDD), U2.33 (IOVDD), U2.42 (IOVDD), U2.43 (ADC_AVDD), U2.44 (VREG_IN), U2.48 (USB_VDD), U2.49 (IOVDD); also elsewhere on the board
/MCU/ALERT#: U2.14 (GPIO11); also elsewhere on the board
/MCU/D_{+}: R4.2; also elsewhere on the board
/MCU/D_{-}: R6.2; also elsewhere on the board
/MCU/GPIO_{0}: J1.8, U2.18 (GPIO15)
/MCU/GPIO_{1}: J1.10, U2.17 (GPIO14)
/MCU/IS31_{BM}: U2.3 (GPIO1); also elsewhere on the board
/MCU/IS31_{EN}: U2.2 (GPIO0); also elsewhere on the board
/MCU/LTC44_{CURR}: U2.39 (GPIO27_ADC1); also elsewhere on the board
/MCU/LTC44_{EN}: U2.40 (GPIO28_ADC2); also elsewhere on the board
/MCU/LTC44_{SEL}: U2.38 (GPIO26_ADC0); also elsewhere on the board
/MCU/LTC44_{~PFO}: U2.41 (GPIO29_ADC3); also elsewhere on the board
/MCU/MISO: U2.31 (GPIO20); also elsewhere on the board
/MCU/MOSI: U2.35 (GPIO23); also elsewhere on the board
/MCU/QSPI_{CLK}: JP1.2 (B), U1.6 (CLK), U2.52 (QSPI_SCLK)
/MCU/QSPI_{D0}: U1.5 (DI(IO0)), U2.53 (QSPI_SD0)
/MCU/QSPI_{D1}: U1.2 (DO(IO1)), U2.55 (QSPI_SD1)
/MCU/QSPI_{D2}: U1.3 (IO2), U2.54 (QSPI_SD2)
/MCU/QSPI_{D3}: U1.7 (IO3), U2.51 (QSPI_SD3)
/MCU/QSPI_{~CS}: R5.2, U1.1 (~CS), U2.56 (QSPI_SS)
/MCU/SCL: U2.5 (GPIO3); also elsewhere on the board
/MCU/SCLK: U2.34 (GPIO22); also elsewhere on the board
/MCU/SDA: U2.4 (GPIO2); also elsewhere on the board
/MCU/TMC_{DIR}: U2.29 (GPIO18); also elsewhere on the board
/MCU/TMC_{EN}: U2.28 (GPIO17); also elsewhere on the board
/MCU/TMC_{STEP}: U2.30 (GPIO19); also elsewhere on the board
/MCU/TMC_{~CS}: U2.32 (GPIO21); also elsewhere on the board
/MCU/~RESET: J1.6, R3.2, SW1.3 (K), SW1.4 (A), U2.26 (RUN)
GND: C1.2, C2.2, C3.2, C4.2, C5.2, C6.2, C7.2, C8.2, C9.2, C10.2, C11.2, C12.2, C13.2, C14.2, C15.2, J1.5, J1.7, J1.9, JP1.1 (A), SW1.1, SW1.2, U1.4 (GND), U2.19 (TESTEN), U2.57 (GND), Y1.2, Y1.4; also elsewhere on the board
unnamed: C15.1, R7.2, Y1.1
unnamed: J1.2, U2.25 (SWD)
unnamed: J1.4, U2.24 (SWCLK)
unnamed: R6.1, U2.46 (USB_DM)
unnamed: R4.1, U2.47 (USB_DP)
unnamed: C1.1, C2.1, C3.1, U2.23 (DVDD), U2.45 (VREG_VOUT), U2.50 (DVDD)
unnamed: C14.1, U2.20 (XIN), Y1.3
unnamed: R7.1, U2.21 (XOUT)

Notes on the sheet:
NB: Place resistors close to pins 46 & 47
NB: Place 1uF close to pin 44
NB: Place 1uF close to pin 45
rp2040 hardware design guide pdf: https://datasheets.raspberrypi.com/rp2040/hardware-design-with-rp2040.pdf minimial viable rp2040 design kicad project: https://www.raspberrypi.com/documentation/microcontrollers/silicon.html#design-files
Table 2 from Section 1.4.3. GPIO Functions, page 13

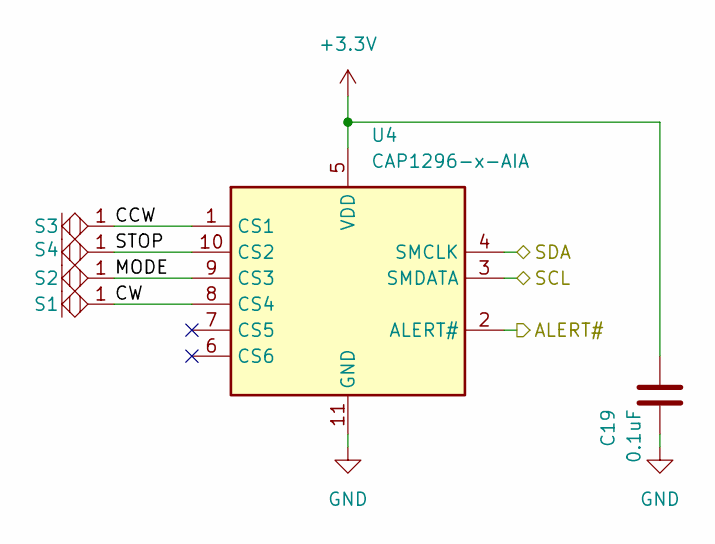
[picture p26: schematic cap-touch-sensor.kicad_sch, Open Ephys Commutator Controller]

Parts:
C19: 0.1uF; C_0402_1005Metric
S1, S2, S3, S4: Touch_Center_2mm
U4: CAP1296-x-AIA; DFN-10-1EP_3x3mm_P0.5mm_EP1.55x2.48mm

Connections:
+3.3V: C19.1, U4.5 (VDD); also elsewhere on the board
/MCU/ALERT#: U4.2 (ALERT#); also elsewhere on the board
/MCU/SCL: U4.3 (SMDATA); also elsewhere on the board
/MCU/SDA: U4.4 (SMCLK); also elsewhere on the board
/Touch Sensors/CCW: S3.1, U4.1 (CS1)
/Touch Sensors/CW: S1.1, U4.8 (CS4)
/Touch Sensors/MODE: S2.1, U4.9 (CS3)
/Touch Sensors/STOP: S4.1, U4.10 (CS2)
GND: C19.2, U4.11 (GND); also elsewhere on the board

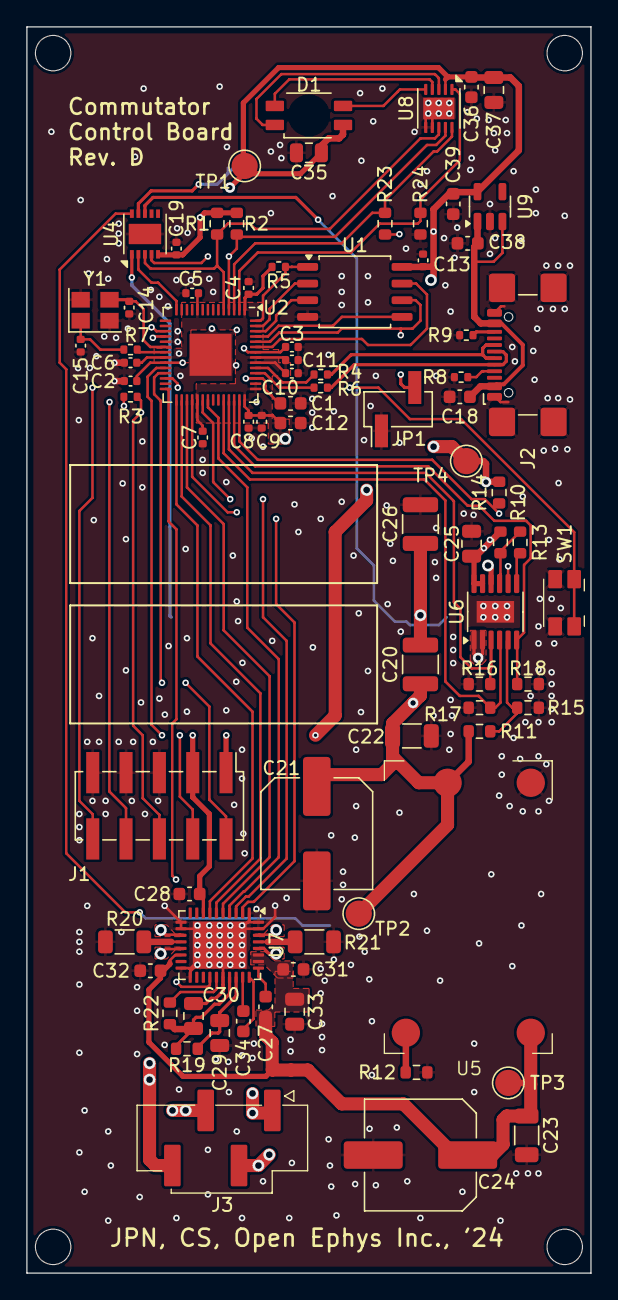
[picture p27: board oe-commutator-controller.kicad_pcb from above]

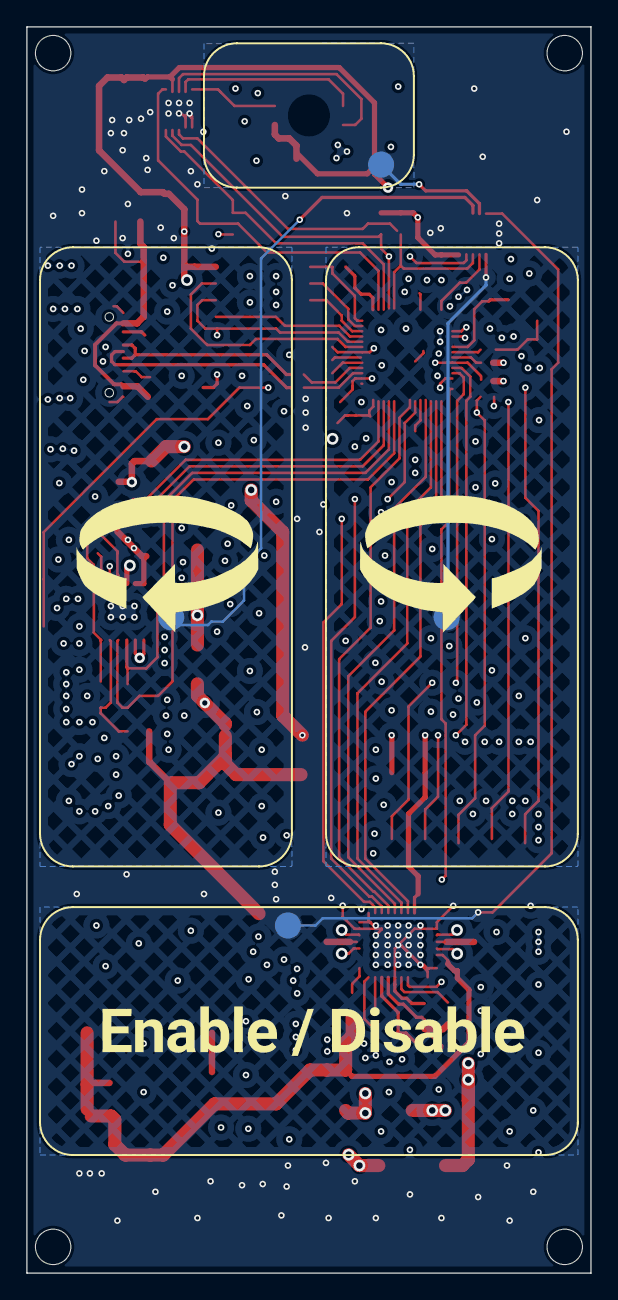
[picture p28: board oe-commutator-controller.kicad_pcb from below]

Board: 4 copper layers, 43.0 x 95.0 mm, 88 parts (4 on the bottom side), 66 nets.

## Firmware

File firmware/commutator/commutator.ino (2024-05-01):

#include <AccelStepper.h>
#include <ArduinoJson.h>
#include <EEPROM.h>
#include <SPI.h>
#include <i2c_t3.h>
#include <math.h>

/////////////////////////////////////////////////////////////////////////////////
// OPTIONS
/////////////////////////////////////////////////////////////////////////////////

// Firmware Version
#define FIRMWARE_VER        "1.6.0"

// 1. Uncomment to continuously dump button press data over Serial
//#define DEBUG

// 2. Select teensy type
#define TEENSYLC
//#define TEENSY32

// 3. Select a commutator type by uncommenting one of the following
//#define COMMUTATOR_TYPE     "SPI Rev. A"
//#define GEAR_RATIO          1.77777777778

#define COMMUTATOR_TYPE     "Single Channel Coax Rev. A"
#define GEAR_RATIO          2.0

//#define COMMUTATOR_TYPE     "Dual Channel Coax Rev. A"
//#define GEAR_RATIO          3.06666666667

/////////////////////////////////////////////////////////////////////////////////
// CONSTANTS
/////////////////////////////////////////////////////////////////////////////////

// Stepper parameters
#define DETENTS             200
#define USTEPS_PER_STEP     8
#define USTEPS_PER_REV      (DETENTS * USTEPS_PER_STEP)
#define MAX_TURNS           (2147483647 / USTEPS_PER_REV / GEAR_RATIO)

// Turn speed and acceleration
#define SPEED_RPM           100
#define ACCEL_RPMM          150
#define MAX_SPEED_SPS       ((float)USTEPS_PER_REV * GEAR_RATIO * SPEED_RPM / 60.0)
#define MAX_ACCEL_SPSS      ((float)USTEPS_PER_REV * GEAR_RATIO * ACCEL_RPMM / 60.0)

// Motor driver parameters
#define MOTOR_POLL_T_US     20

// Capacitive touch buttons
#define CAP_TURN_CW         0
#define CAP_MODE_SEL        1
#define CAP_TURN_CCW        15
#define CAP_STOP_GO         17

// Stepper driver pins
#define MOT_DIR             14
#define MOT_STEP            16
#define MOT_CFG0_MISO       12
#define MOT_CFG1_MOSI       11
#define MOT_CFG2_SCLK       13
#define MOT_CFG3_CS         10
#define MOT_CFG6_EN         9

// Power options
#define MOT_POW_EN          22
#define VMID_SEL            20
#define CHARGE_CURR         21
#define nPOW_FAIL           23
#define CHARGE_CURR_THRESH  0.06 // Super capacitor charge current, in Amps, that must be reached to transistion to normal operation.
#define RPROG               2000.0 // Charge current programming resistor (Ohms)
#define CODE_TO_AMPS        (3.3 / 1024 * 1000.0 / RPROG)

// I2C
#define SDA                 18
#define SCL                 19

// RGB Driver
#define IS31_ADDR           0x68
#define IS31_SHDN           5
#define IS31_BM             2

// TMC2130 registers
#define WRITE_FLAG          (1<<7)
#define READ_FLAG           (0<<7)
#define REG_GCONF           0x00
#define REG_GSTAT           0x01
#define REG_IHOLD_IRUN      0x10
#define REG_CHOPCONF        0x6C
#define REG_COOLCONF        0x6D
#define REG_DCCTRL          0x6E
#define REG_DRVSTATUS       0x6F
#define REG_PWMCONF         0x70

// Settings address start byte
#define SETTINGS_ADDR_START 0
#define CAP_ADDR_START      0x0F

// Controller state
struct Context {
    int led_on = 1; // Using a bool results in extemely bizarre behavior
    int commutator_en = 1;  // Using a bool results in extemely bizarre behavior
};

// Holds the current state
Context ctx;

// Save settings flag
int save_required = 0;

// Stepper motor
AccelStepper motor(AccelStepper::DRIVER, MOT_STEP, MOT_DIR);
double target_turns = 0;

// Motor update timer
IntervalTimer mot_timer;

// I was touched..., by the power..., on my unit..., in broooooooooooad
// daylight
enum TouchState { untouched, held };

struct TouchSensor {

    // Result
    TouchState result = untouched;

    // Physical constants
    const int pin = 0;

    // Algorithm state
    int last = 0;
    float i = 0;
    const int i_thresh = 400;
    int d_thresh = 0;
    int fresh = 1;
};

// Touch Sensors with pre-measured estimates for capacitance of each button
#ifdef TEENSYLC
TouchSensor touch_cw {.pin = CAP_TURN_CW, .last = 12000, .d_thresh = 8};
TouchSensor touch_ccw {.pin = CAP_TURN_CCW, .last = 12100, .d_thresh = 8};
TouchSensor touch_mode {.pin = CAP_MODE_SEL, .last = 2700, .d_thresh = 2};
TouchSensor touch_stopgo {.pin = CAP_STOP_GO, .last = 10700, .d_thresh = 10};
#endif

#ifdef TEENSY32
TouchSensor touch_cw {.pin = CAP_TURN_CW, .last = 12000, .d_thresh = 15};
TouchSensor touch_ccw {.pin = CAP_TURN_CCW, .last = 12100, .d_thresh = 15};
TouchSensor touch_mode {.pin = CAP_MODE_SEL, .last = 2700, .d_thresh = 3};
TouchSensor touch_stopgo {.pin = CAP_STOP_GO, .last = 10700, .d_thresh = 15};
#endif

void check_touch(TouchSensor *sensor)
{
    int m = touchRead(sensor->pin);
    int d =  m - sensor->last;
    sensor->last = m;
    auto last_state = sensor->result;

    if (abs(d) > sensor->d_thresh)
        sensor->i += (float)d;

    if (sensor->i > sensor->i_thresh)
    {
        sensor->result = held;
    } else {
        sensor->i *=  0.9;
        sensor->result = untouched;
    }

    sensor->fresh = last_state != sensor->result;
}

uint8_t tmc_write(uint8_t cmd, uint32_t data)
{
    uint8_t s;

    digitalWriteFast(MOT_CFG3_CS, LOW);

    s = SPI.transfer(cmd);
    SPI.transfer((data >> 24UL) & 0xFF);
    SPI.transfer((data >> 16UL) & 0xFF);
    SPI.transfer((data >> 8UL) & 0xFF);
    SPI.transfer((data >> 0UL) & 0xFF);

    digitalWriteFast(MOT_CFG3_CS, HIGH);

    return s;
}

uint8_t tmc_read(uint8_t cmd, uint32_t *data)
{
    uint8_t s;

    tmc_write(cmd, 0UL); // set read address

    digitalWriteFast(MOT_CFG3_CS, LOW);

    s = SPI.transfer(cmd);
    *data = SPI.transfer(0x00) & 0xFF;
    *data <<= 8;
    *data |= SPI.transfer(0x00) & 0xFF;
    *data <<= 8;
    *data |= SPI.transfer(0x00) & 0xFF;
    *data <<= 8;
    *data |= SPI.transfer(0x00) & 0xFF;

    digitalWriteFast(MOT_CFG3_CS, HIGH);

    return s;
}

// Setting state load/save
void load_settings()
{
    int addr = SETTINGS_ADDR_START;

    byte good_settings = 0x0;
    EEPROM.get(addr, good_settings); // check good settings flag
    if (good_settings != 0x12)
        return;

    EEPROM.get(addr += sizeof(int), ctx);
}

// Save enable and LED state
void save_settings()
{
    int addr = SETTINGS_ADDR_START;
    EEPROM.put(addr, 0x12); // good settings flag
    EEPROM.put(addr += sizeof(int), ctx);
}

// Motor target update. We integrate turns in the target position and apply to
// motor's motion.
void turn_commutator(double turns)
{
    // Invalid request
    if (abs(turns) > MAX_TURNS)
        return; // Failure, cant turn this far

    // Relative move
    target_turns += turns;

    if (abs(target_turns) < MAX_TURNS)
    {
        motor.moveTo(lround(target_turns * (double)USTEPS_PER_REV * GEAR_RATIO));
    } else {
        // Deal with very unlikely case of overflow
        soft_stop();
        turn_commutator(turns); // Restart this routine now that position has been zeroed
    }
}

// Emergency motor stop/reset
void hard_stop()
{
    motor.setAcceleration(1e6);
    motor.stop();
    motor.runToPosition();
    motor.setCurrentPosition(0);
    target_turns = 0.0;
    motor.setAcceleration(MAX_ACCEL_SPSS);
}

void soft_stop()
{
    motor.setCurrentPosition(0);
    target_turns = 0.0;
}

void set_rgb_color(byte r, byte g, byte b)
{
    // Set PWM state
    Wire.beginTransmission(IS31_ADDR);
    Wire.write(0x04);
    Wire.write(r);
    Wire.write(g);
    Wire.write(b);
    Wire.endTransmission();

    // Update PWM
    Wire.beginTransmission(IS31_ADDR);
    Wire.write(0x07);
    Wire.write(0x00);
    Wire.endTransmission();
}

void update_rgb()
{
    if (!ctx.led_on) {
        set_rgb_color(0x00, 0x00, 0x00);
        return;
    }

    if (!ctx.commutator_en) {
        set_rgb_color(255, 0, 0);
        return;
    }

    set_rgb_color(1, 20, 7);
}

void setup_rgb()
{
    // I2C for RGB LED
    Wire.begin(I2C_MASTER, 0x00, I2C_PINS_18_19, I2C_PULLUP_EXT, 400000);
    Wire.setDefaultTimeout(200000); // 200ms

    // Enable LED current driver
    digitalWriteFast(IS31_SHDN, HIGH);
    delay(1);

    // Set max LED current
    Wire.beginTransmission(IS31_ADDR);
    Wire.write(0x03);
    Wire.write(0x08); // Set max current to 5 mA
    Wire.endTransmission();

    // Default color
    update_rgb();

    // Enable current driver
    Wire.beginTransmission(IS31_ADDR);
    Wire.write(0x00);
    Wire.write(0x20); // Enable current driver
    Wire.endTransmission();
}

void setup_io()
{
    pinMode(MOT_CFG6_EN, OUTPUT);
    pinMode(MOT_DIR, OUTPUT);
    pinMode(MOT_STEP, OUTPUT);
    pinMode(MOT_CFG3_CS, OUTPUT);
    pinMode(MOT_CFG1_MOSI, OUTPUT);
    pinMode(MOT_CFG0_MISO, INPUT);
    pinMode(MOT_CFG2_SCLK, OUTPUT);

    pinMode(MOT_POW_EN, OUTPUT);
    pinMode(VMID_SEL, OUTPUT);
    pinMode(nPOW_FAIL, INPUT);

    pinMode(IS31_SHDN, OUTPUT);
}

inline void motor_driver_en(int enable)
{
    digitalWriteFast(MOT_CFG6_EN, enable ? LOW : HIGH); // Inactivate driver (LOW active)
}

void setup_motor()
{
    // Default state
    motor_driver_en(0);
    digitalWriteFast(MOT_DIR, LOW); // LOW or HIGH
    digitalWriteFast(MOT_STEP, LOW);

    digitalWriteFast(MOT_CFG3_CS, HIGH);
    digitalWriteFast(MOT_CFG1_MOSI, LOW);
    digitalWriteFast(MOT_CFG0_MISO, HIGH);
    digitalWriteFast(MOT_CFG2_SCLK, LOW);

    // init SPI
    SPI.begin();
    SPI.beginTransaction(SPISettings(1000000, MSBFIRST, SPI_MODE3));

    // TMC2130 config
    // voltage on AIN is current reference
    // Stealthchop is on
    tmc_write(WRITE_FLAG | REG_GCONF, 0x00000007UL);

    // Configure steathchip
    // PWM_GRAD = 0x0F
    // PWM_AMPL = 0xFF
    // pwm_autoscale = 0x01
    tmc_write(WRITE_FLAG | REG_PWMCONF, 0x00040FFFUL);

    // IHOLD = 0x0A
    // IRUN = 0x1F (Max)
    // IHOLDDELAY = 0x06
    tmc_write(WRITE_FLAG | REG_IHOLD_IRUN, 0b01100001111100011111UL); // 0x00_04_1F_UL);

    switch (USTEPS_PER_STEP) {
        case 1:
            tmc_write(WRITE_FLAG | REG_CHOPCONF, 0x08008008UL); //  1 microsteps,
            break;
        case 2:
            tmc_write(WRITE_FLAG | REG_CHOPCONF, 0x07008008UL); //  2 microsteps,
            break;
        case 4:
            tmc_write(WRITE_FLAG | REG_CHOPCONF, 0x06008008UL); //  4 microsteps,
            break;
        case 8:
            tmc_write(WRITE_FLAG | REG_CHOPCONF, 0x05008008UL); //  8 microsteps,
            break;
        case 16:
            tmc_write(WRITE_FLAG | REG_CHOPCONF, 0x04008008UL); // 16 microsteps,
            break;
        case 32:
            tmc_write(WRITE_FLAG | REG_CHOPCONF, 0x03008008UL); // 32 microsteps,
            break;
        case 64:
            tmc_write(WRITE_FLAG | REG_CHOPCONF, 0x02008008UL); // 64 microsteps,
            break;
        case 128:
            tmc_write(WRITE_FLAG | REG_CHOPCONF, 0x01008008UL); //128 microsteps,
            break;
        default:
            tmc_write(WRITE_FLAG | REG_CHOPCONF, 0x08008008ul); //  1 microsteps,
            break;
    }

    // Set speed and accel
    motor.setMaxSpeed(MAX_SPEED_SPS);
    motor.setAcceleration(MAX_ACCEL_SPSS);

    // Minimum pulse width
    motor.setMinPulseWidth(3);

    // Setup run() timer
    mot_timer.begin(run_motor_isr, MOTOR_POLL_T_US);

    // Activate motor
    motor_driver_en(1);
}

void run_motor_isr()
{
    if (motor.distanceToGo() != 0) {
        motor.run();
    }
}

void setup_power()
{
    // Turn on breathing mode
    set_rgb_color(255, 0, 0);
    Wire.beginTransmission(IS31_ADDR);
    Wire.write(0x02);
    Wire.write(0x20); // Turn on breathing mode
    Wire.endTransmission();

    // Turn on the motor power
    digitalWriteFast(MOT_POW_EN, HIGH);
    delay(100);

    // NB: Set 2.7V across each super cap
    digitalWriteFast(VMID_SEL, HIGH);

    // Wait for charge current stabilize and breath LED in meantime
    while (digitalRead(nPOW_FAIL) == LOW)
      delay(10);

    Wire.beginTransmission(IS31_ADDR);
    Wire.write(0x02);
    Wire.write(0x00); // Turn off breathing mode
    Wire.endTransmission();
}

inline float charge_current()
{
    return CODE_TO_AMPS * analogRead(CHARGE_CURR);
}
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

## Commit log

2018-12-17 initial commit 3d layout
    [6627T370_POSITION-CONTROL DC MOTOR.SLDPRT, CUI_PJ-102A.SLDPRT, CUI_PJ-102A.STEP, DRV 8825 With Headers Assem.SLDPRT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]
2018-12-17 tweaked mounting
    [rf_commutator_housing.SLDPRT]
2018-12-18 updated commuttaor to use flanged rotary joint
    [Fairview_FMRJ1002_rf_rotary_jpint_female_to_female_flanged.SLDPRT, gear_a.SLDPRT, rf_commutator_housing.SLDPRT]
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2018-12-19 updated various parts
    [gear_a.SLDPRT, gear_a.STL, gear_b.STL, rf_commutator_housing.SLDPRT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]
2019-01-07 Progress on commutator control board
    - Schematic is about complete with the exception of digital signal
    wiring, which should be done interactively to detangle wires
    - Added datasheets
    - Basic component placement
    [commutator-controller.brd, commutator-controller.sch]
2019-01-07 Made housing 95mm tall to fit PCB
    [rf_commutator_housing.SLDPRT, rf_commutator_housing.STL]
2019-01-09 Nearly complete control board
    - Silkscreen still needs work: button labels, device label, etc
    [commutator-controller.brd, commutator-controller.sch]
2019-01-09 Completed control board
    - Pending review from jvoigts
    [commutator-controller.GBL, commutator-controller.GBO, commutator-controller.GBS, commutator-controller.GKO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]
2019-01-09 Small updates to control-board after review
    - Made sense of rotation direction icons less ambiguous and swapped
    positions
    - Moved push button back a bit
    - Remove copper layer between LED and top side of board
    [commutator-controller.GBL, commutator-controller.GBO, commutator-controller.GTL, commutator-controller.GTO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]
2019-01-10 Added stop/go button to control board
    - Added README
    [commutator-controller.GBL, commutator-controller.GBO, commutator-controller.GTL, commutator-controller.GTO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]
2019-01-10 Added fourth mode button on control board
    - Sits around RGB LED window
    - Also, increased min via drill size to 0.3mm which greatly decreases
    board cost
    [commutator-controller.GBL, commutator-controller.GBO, commutator-controller.GTL, commutator-controller.GTO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]
2019-01-10 Updated housing and gears - Added cutouts for teensy and reset switch - Made PCB housing deeper - Fixed mounting screw features - Added keyed features to gears - Reduced rotary joint gear ID to match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
    [gear_a.SLDPRT, gear_a.STL, gear_b.STL, rf_commutator_housing.SLDPRT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]
2019-01-31 Adjusted id of larger gear to better fit commutator
    [gear_b.STL]
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2019-02-01 Firmware updates and repo cleanup
    - Firware updates: manual, remote, and both control states now
    - Made all parameter values output referenced (to take care of 2x gear
    reduction)
    - Moved mechanical stuff to mechanical folder
    [6627T370_POSITION-CONTROL DC MOTOR.SLDPRT, CUI_PJ-102A.SLDPRT, CUI_PJ-102A.STEP, DRV 8825 With Headers Assem.SLDPRT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]
2019-02-02 Updates to README, firmware, and control-board
    - Fixed mirrored pads for super capacitor charger
    - Switched Teensy LC for Teensy 3.2
    - Moved Teensy in 2mm so that housing does not need large cutout, but
    small one for micro USB
    - Fixed other small issues with the circuit
    - Some small changed to firmware: speed now provided directly in RPM
    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
    [commutator-controller.GBL, commutator-controller.GBO, commutator-controller.GTL, commutator-controller.GTO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]
2019-02-04 Tweaks to commutator housing - Made pcb compartment in housing deeper - Added extra height to bottom part so it can stand on surface
    [rf_commutator_housing.SLDPRT, rf_commutator_housing.STL]
2019-06-25 updated gear to fit the spinner RF joint
    [gear_b.STL, spinner_BN-835047C0010_rf_rotary_joint.SLDPRT]
2019-09-13 Fix charging bug in firmware
    - The controller appeared to be unresponsive because it was not
    reporting when it was charging the supercaps. This commit fixes that
    - Also, I now turn off the controller 0.5 sec after the target turn has
    gone to 0. This may be a bad idea due to error accumulation.
    - Update the schematic of controller and provide new pdf
    [commutator-controller.brd, commutator-controller.sch]
2019-09-22 Update gear_b.stl to match the current part
    - Fits the German rf rotary joint
    [gear_b.STL]
2019-12-12 added dual channel doc
    [6627T370_POSITION-CONTROL DC MOTOR.SLDPRT, CUI_PJ-102A.SLDPRT, CUI_PJ-102A.STEP, DRV 8825 With Headers Assem.SLDPRT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]
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2019-12-23 WIP 2 channel commutator
    [6627T370_POSITION-CONTROL DC MOTOR.SLDPRT, BN_153127C0001_rotary_joint.SLDPRT, CUI_PJ-102A.SLDPRT, DRV 8825 With Headers Assem.SLDPRT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]
2019-12-24 initial design of dual-channel commutator housing
    [dual_channel_commutator_housing.SLDPRT]
2020-01-17 Mechanical updates and added STLs
    [dual_channel_commutator_housing.SLDPRT, dual_channel_commutator_housing.STL, gear_b_dual_channel.STL]
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2020-09-26 Small changes to the commutator driver board
    - No change in BOM or functionality
    - Added silkscreen outline to LED touch pad
    - Added OE logo
    - Remove license from silkscreen
    [commutator-controller.GBL, commutator-controller.GBO, commutator-controller.GBS, commutator-controller.GTL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]
2021-04-22 Small fixes to control board for production
    - Vias under LED driver were not symmetrical which caused delta-T during
    reflow and therefore bad settling of device. I made them symmetrical
    - Removed a couple random copper lines
    [commutator-controller.GBL, commutator-controller.GTL, commutator-controller.XLN, commutator-controller.brd]
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2023-03-24 add SPI enclosure prototype CAD files
    [6627T370_POSITION-CONTROL DC MOTOR.SLDPRT, 91292A191_18-8 Stainless Steel Socket Head Screw.SLDPRT, 92196A105_18-8 Stainless Steel Socket Head Screw.SLDPRT, SI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]
2023-04-04 jon revisions + enclosed motor
    [11HS20-0674S.SLDPRT, SI_sdpsi_s12a05m054n0310 cut.SLDPRT, SI_sdpsi_s12a05m054n0310.stp, SI_sdpsi_s12a05m096n0310 cut.SLDPRT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]
2023-04-04 stl/step files for producing gears
    [SI_sdpsi_s12a05m054n0310 cut.STEP, SI_sdpsi_s12a05m054n0310 cut.STL, SI_sdpsi_s12a05m096n0310 cut.SLDPRT, SI_sdpsi_s12a05m096n0310 cut.STEP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]
2023-04-05 added clearance for gear
    [SPI Commutator Enclosure Motor Enclosed.SLDPRT, SPI Commutator Enclosure Motor Enclosed.STEP, SPI Commutator Enclosure Motor Enclosed.STL]
2023-04-10 45 deg bevelled gear
    [SI_sdpsi_s12a05m054n0310 cut.SLDPRT, SI_sdpsi_s12a05m054n0310 cut.STEP, SI_sdpsi_s12a05m054n0310 cut.STL, SI_sdpsi_s12a05m096n0310 cut.STEP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]
2023-07-17 jon's changes
    fillets added. I think this version was printed and sent
    [SI_sdpsi_s12a05m054n0310 cut.SLDPRT, SI_sdpsi_s12a05m054n0310 cut.STEP, SI_sdpsi_s12a05m054n0310 cut.STL, SI_sdpsi_s12a05m096n0310 cut.STEP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]
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2023-09-11 createad notch for power button per production team's request
    [SPI Commutator Enclosure Motor Enclosed.STEP, SPI Commutator Enclosure Motor Enclosed.STL]
2023-09-14 widened m2.5 clearance holes for mounting nema stepper motor (2.7mm->3mm)
    [SPI Commutator Enclosure Motor Enclosed.SLDPRT, SPI Commutator Enclosure Motor Enclosed.STEP, SPI Commutator Enclosure Motor Enclosed.STL]
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2023-11-21 Control board rev. C
    - Move to KiCAD
    - Replace silent stepper stick with on-board circuit
    [commutator-controller.GBL, commutator-controller.GBO, commutator-controller.GBS, commutator-controller.GKO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]
2023-12-06 Board revision C
    - Sent to JLCPCB for testing
    [oe-commutator-controller-B_Cu.gbr, oe-commutator-controller-B_Fab.gbr, oe-commutator-controller-B_Mask.gbr, oe-commutator-controller-B_Paste.gbr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]
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2024-01-23 Increase R_prog to 2.49k
    - This accounts for overhead current drawn from VCC by the Teensy and
    LED driver
    [oe-commutator-controller.kicad_pcb, oe-commutator-controller.kicad_sch]
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2024-09-19 Update dual channel commutator enclosure
    - Enclose motor
    - Improve PCB mounting
    - Remove large hole that exposed Teensy
    [BN_153127C0001_rotary_joint.SLDPRT, dual_channel_commutator_housing.SLDPRT, dual_channel_commutator_housing.STL, gear_b_dual_channel.STL]
2024-09-26 Rev D Schematic
    - split schematic into several pages
    - replace teensy with rp2040
    - Add dedicated capacititave touch sensor ic
    - Replacec Micro-Usb with USB-C
    [cap-charger.kicad_sch, cap-sensor.kicad_sch, cap-touch-sensor.kicad_sch, mcu-flash.kicad_sch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]
2024-09-26 Remove redundant file
    [cap-sensor.kicad_sch]
2024-09-26 Replaced through-hole components with SMD
    - Other small edits (e.g. optional jumper to force USB-boot)
    [cap-charger.kicad_sch, cap-touch-sensor.kicad_sch, mcu-flash.kicad_sch, motor-driver.kicad_sch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]
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2024-09-27 Rev D PCB WIP for Review
    - Before going into further minutiae, get review
    - Components are laid out and routed
    - Fails DRC check, requires vias for better GND plane, there are traces
    in the outer keepout zone, remove S5?
    [cap-touch-sensor.kicad_sch, mcu-flash.kicad_sch, oe-commutator-controller.kicad_pcb, rgb-driver.kicad_sch]
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
